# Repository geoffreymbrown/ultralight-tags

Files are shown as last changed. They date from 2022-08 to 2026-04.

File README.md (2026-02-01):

See [Documentation](https://geoffreymbrown.github.io/ultralight-tags/) to explore this project and for complete build instructions.

# building with OS X

cmake  -DQt6_DIR=/Users/geobrown/Qt/6.5.3/macos  ~/Research/ultralight-tags 

Make sure to add Qt-version/bin (or current version) to your path so that the various find_program tools work (esp macdeployqt)

(use your signing authority)

macdeployqt bin/btviz.app -codesign="Indiana University"
macdeployqt bin/qtmonitor.app -codesign="Indiana University (5J69S77A7G)"
macdeployqt bin/tag-test.app -codesign="Indiana University"
        
To verify

codesign --verify --deep --verbose xyz.app

Then build the dmg file

cpack -G DragNDrop

No longer building qt -- using distributed version
-------------

Building QT

https://doc.qt.io/qt-6/macos-building.html

_ ./configure -- -DCMAKE_OSX_ARCHITECTURES="x86_64h;arm64"

Install	macports

sudo port install libusb-1.0
#sudo port install qt6

# building with MSVC

you have my deepest sympathy

## For building host software    

* install vcpkg -- within vcpkg:
  * install protobuf --- vcpkg.exe install protobuf --triplet=x64-windows-static
  * install qt:x64-windows-static
  * install libusb:x64-windows-static
  * install ms-angle:x64-windows-static
* install nanopb binary  -- unpack in root_dir/nanopb ;   using the binary version is more reliable than using the source version
* install pkg-config choco install pkgconfiglite -y

**Note** cmake now understands vcpkg so the direct installation within vcpkg is no longer needed.   Instead there are json files in the ultralight-tags directory that cmake uses in install vcpkg files.

### Configure main build

cmake -DVCPKG_TARGET_TRIPLET="x64-mingw-static" -G "MinGW Makefiles" -DCMAKE_TOOLCHAIN_FILE="d:/vcpkg/scripts/buildsystems/vcpkg.cmake" c:/Users/geobrown/ultralight-tags

**Note** cmake has trouble on windows finding Qt.  The workaround is to use qt-cmake from the qt installation.

```
  cmake -DVCPKG_TARGET_TRIPLET="x64-windows-static" -DCMAKE_TOOLCHAIN_FILE="c:/users/geoff/vcpkg/scripts/buildsystems/vcpkg.cmake" c:/Users/geoff/ultralight-tags
```

```
qt-cmake -B Build -S c:\users\geobrown\ultralight-tags --preset default -G "Visual Studio 17 2022"
```

### Build release/debug

```
cmake --build . --config Debug  
cmake --build . --config Release
```

## Building Embedded Software

* install ChibiOS (submodule in repo)
* install gnu-arm toolchain
* install java
* install fmpp
* install make (choco)

### Building Tags

```
cmake --build . --target [BitTagv6|BitTagv5|BitTagNucleo]
cmake --build . --target BitTagv6-download

```

### Building Base boards

```
cmake --build . --target bittag-base-jlcpcb-v3
cmake --build . --target bittag-base-jlcpcb-v3-dfu
cmake --build . --target tag-breakout-base-jlcpcb32-v1
cmake --build . --target tag-breakout-base-jlcpcb32-v1-dfu
```

 The -dfu rule attempts to  program the board.

## Programming Embedded Hardware

* Install [stm32cube programmer](https://wiki.st.com/stm32mpu/wiki/STM32CubeProgrammer)

## Programming with STM32Cube Programmer

```
~/Software/STM32CubeProgrammer/bin/STM32_Programmer_CLI.exe -c port=SWD mode=UR -d ch.elf -v -g 0x08000000 
```

* `port=SWD` driver
* `mode=UR` -- attach under reset
* `-g 0x08000000`  -- execute program after completion
* `-v` verify
* `-vb 3`  verbose logging (for debugging)

### DFU for base boards

Make sure a device is in dfu mode

```
STM32_Programmer_CLI.exe -l usb
```

To program from command line

```
 ~/Software/STM32CubeProgrammer/bin/STM32_Programmer_CLI -c port=usb1 -d build/ch.elf 
 ```

## Installing protobuf on linux

```
git clone https://github.com/google/protobuf.git
cd protobuf
configure
make 
sudo make install
mkdir build
cd build
cmake ../cmake
make
sudo make install
```

# Tools

## Host and Embedded 

cmake
protobuf -- protoc, libprotobuf, python (pip install protobuf)
nanopb
python

## Host only

Qt5
libusb
vcpkg (windows)

## Embedded only

chibios
fmpp
stm32 programmer cli
arm gcc tools

## Mechanical

openscad 
kicad

## Powershell $Profile

$env:Path += ";C:\Program Files (x86)\GNU Arm Embedded Toolchain\9 2020-q2-update\bin\"
$env:Path += "; C:\Program Files (x86)\Microsoft Visual Studio\2019\Community\VC\Tools\MSVC\14.27.29110\bin\Hostx64\x64\"
$env:Path += "; C:\Program Files (x86)\Microsoft Visual Studio\2019\Community\VC\Tools\MSVC\14.27.29110\bin\Hostx64\x86\"
$env:Path += "; C:\Program Files\fmpp\bin"
$env:Path += "; C:\Program Files\Java\jre1.8.0_261\bin"
$env:Path += "; C:\Program Files\STMicroelectronics\STM32Cube\STM32CubeProgrammer\bin"
$env:Path += "; C:\Program Files (x86)\Microsoft Visual Studio\2019\Community\SDK\ScopeCppSDK\vc15\SDK\bin"

# Notes on universal binary

cmake ~/Research/ultralight-tags    -DCMAKE_OSX_ARCHITECTURES="x86_64;arm64" -DCMAKE_OSX_DEPLOYMENT_TARGET="12.3"

libusb

 ./configure CFLAGS="-arch x86_64 -arch arm64" CXXFLAGS="-arch x86_64 -arch arm64"

 protobuf

 ./configure CFLAGS="-arch x86_64 -arch arm64" CXXFLAGS="-arch x86_64 -arch arm64"

 # Notes on Building Static qt for windows

 - Download sources
 - use ""x64 Native Tools Command Prompt for VS 2022" for building !!  This is important because otherwise the powershell window will build a 32bit binary
 - 
 - ..\Qt\6.10.2\Src\configure.bat -prefix C:\QT-build\ -static -static-runtime -release -nomake examples -nomake tests --skip qtquick3dphysics --skip qtopcua
 - cmake --build .
 - cmake --install . --prefix c:\Qt6-static

 Fucking Windows 11 opens 32 bit developer powershell by default!  Have to find the 64 bit version in visual studio tools-commandline

 Open the Start Menu and search for the "x64 Native Tools Command Prompt" for your installed version of Visual Studio (e.g., "x64 Native Tools Command Prompt for VS 2022"). This ensures your environment variables are correctly set for a 64-bit build.

 Building for windows 2/1/26

- $env:Qt6_DIR = "C:\Qt6-static\lib\cmake\Qt6\"  
- cmake -DVCPKG_TARGET_TRIPLET="x64-windows-static" -DCMAKE_TOOLCHAIN_FILE="c:/users/geoff/vcpkg/scripts/buildsystems/vcpkg.cmake" -D Qt6_DIR="c:/Qt6-static/lib/cmake/Qt6" c:/Users/geoff/ultralight-tags

- cmake --Build . --config Release  
- cmake --install . --prefix install-directory-path

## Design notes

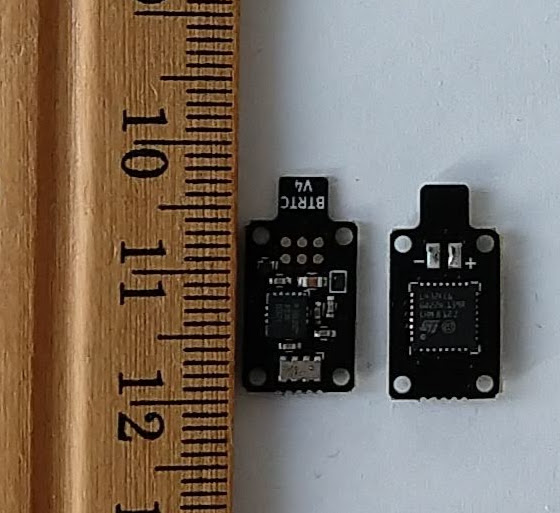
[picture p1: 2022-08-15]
docs/content/en/docs/architecture/images/bittagsbothsides.jpg

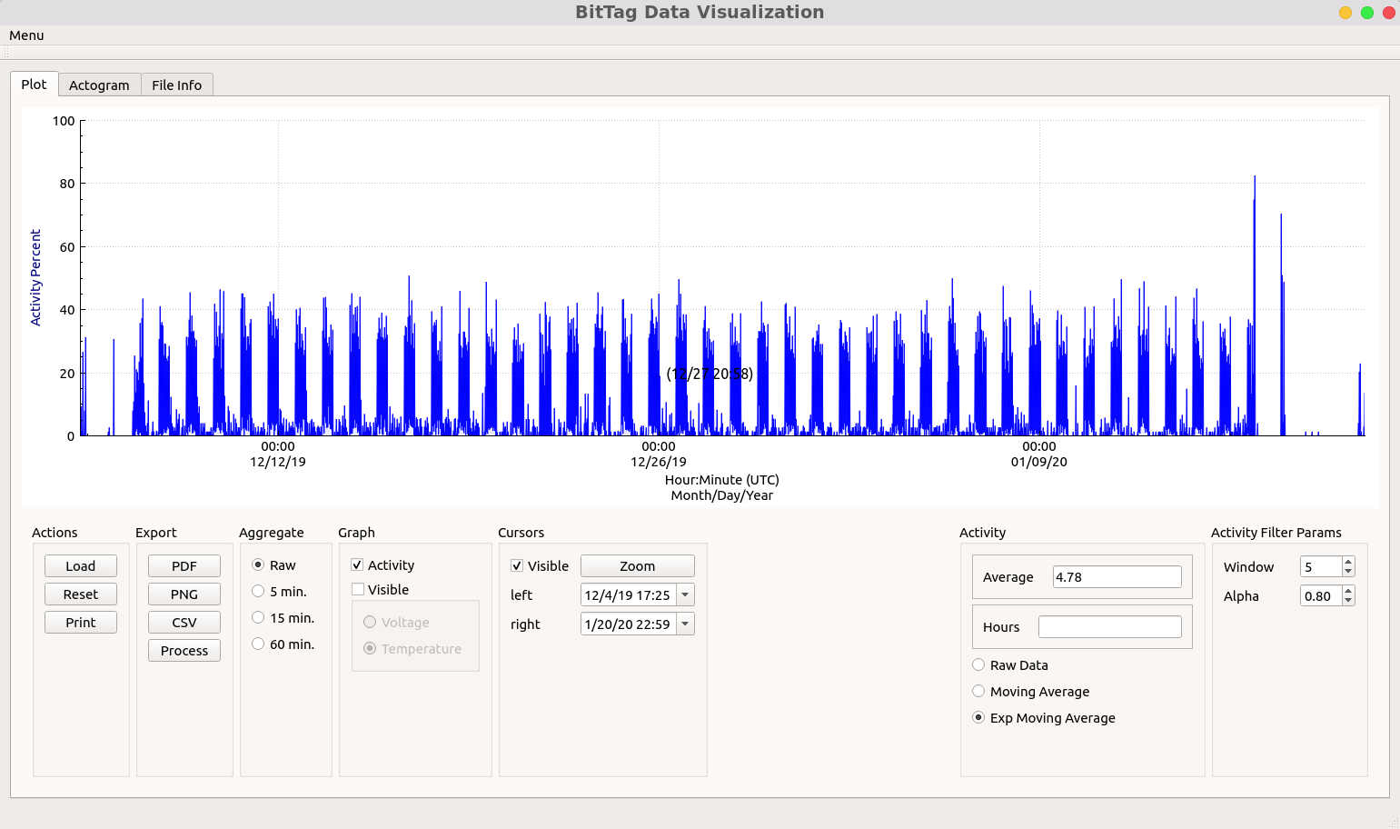
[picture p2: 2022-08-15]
docs/content/en/docs/architecture/images/datavisualization.png

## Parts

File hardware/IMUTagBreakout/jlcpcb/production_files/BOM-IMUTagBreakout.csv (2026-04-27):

Comment | Designator | Footprint | LCSC | Quantity
0.1uf | C1,C10,C2,C5,C6,C7,C8,C9 | C_0603_1608Metric | C14663 | 8
1uf | C3,C4 | C_0603_1608Metric | C15849 | 2
220 | R1,R2 | R_0603_1608Metric | C22962 | 2
AK09940A | U3 | AK09940a | C6794828 | 1
LED | D1,D2 | LED_0603_1608Metric | C2286 | 2
LPS22HH | U5 | ST_HLGA-10_2x2mm_P0.5mm_LayoutBorder3x2y | C2827824 | 1
LSM6DSV16XTR | U4 | LGA-14_3x2.5mm_P0.5mm_LayoutBorder3x4y | C5267406 | 1
MX25L12835G | U2 | SOIC-8_5.3x6.2mm_P1.27mm | C136615 | 1
TPS7A0218PDQNR | U1 | Texas_X2SON-4_1x1mm_P0.65mm | C2862166 | 1

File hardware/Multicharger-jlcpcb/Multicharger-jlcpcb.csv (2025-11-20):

Source: | /home/geobrown/Research/ultralight-tags/hardware/Multicharger-jlcpcb/Multicharger-jlcpcb.kicad_sch
Date: | Sun 09 Jul 2023 01:42:09 PM EDT
Tool: | Eeschema 6.0.11-2627ca5db0~126~ubuntu22.04.1
Generator: | /usr/share/kicad/plugins/bom_csv_grouped_by_value_with_fp.py
Component Count: | 20
Ref | Qnty | Value | Cmp name | Footprint | Description | Vendor
C101, | 1 | 0.1uF | C | Capacitor_SMD:C_0402_1005Metric | Unpolarized capacitor
C106, | 1 | 1uF | C | Capacitor_SMD:C_0402_1005Metric | Unpolarized capacitor
C107, | 1 | 2.2uF | C | Capacitor_SMD:C_0402_1005Metric | Unpolarized capacitor
D101, | 1 | No Go Red | LED | LED_SMD:LED_0603_1608Metric | Light emitting diode
D102, | 1 | BLUE | LED | LED_SMD:LED_0603_1608Metric | Light emitting diode
D103, | 1 | Go Green | LED | LED_SMD:LED_0603_1608Metric | Light emitting diode
D104, D105, | 2 | D_Schottky | D_Schottky | Diode_SMD:D_SOD-323 | Schottky diode
J104, | 1 | USB_B_Mini | USB_B_Mini | Connector_USB:USB_Mini-B_Lumberg_2486_01_Horizontal | USB Mini Type B connector
R1, | 1 | 680 | R | Resistor_SMD:R_0603_1608Metric | Resistor
R101, | 1 | 220 | R | Resistor_SMD:R_0603_1608Metric | Resistor
R102, R105, | 2 | 120 | R | Resistor_SMD:R_0603_1608Metric | Resistor
R103, | 1 | 91K | R | Resistor_SMD:R_0603_1608Metric | Resistor
R104, | 1 | 13K | R | Resistor_SMD:R_0603_1608Metric | Resistor
R106, | 1 | 1500 | R | Resistor_SMD:R_0603_1608Metric | Resistor
R107, | 1 | 2.2K | R | Resistor_SMD:R_0603_1608Metric | Resistor
SW101, | 1 | SW_DIP_x04 | SW_DIP_x04 | Button_Switch_SMD:SW_DIP_SPSTx04_Slide_6.7x11.72mm_W8.61mm_P2.54mm_LowProfile | 4x DIP Switch, Single Pole Single Throw (SPST) switch, small symbol
U101, | 1 | TPS3700 | TPS3700 | Package_TO_SOT_SMD:SOT-23-6
U106, | 1 | XC6206-3.3V | XC6206PxxxMR | Package_TO_SOT_SMD:SOT-23-3 | Positive 60-250mA Low Dropout Regulator, Fixed Output, SOT-23

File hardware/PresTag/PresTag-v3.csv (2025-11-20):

Source: | /home/geobrown/Research/ultralight-tags/hardware/PresTag/PresTag-v3.kicad_sch
Date: | Thu 16 Mar 2023 07:56:26 PM EDT
Tool: | Eeschema 6.0.2+dfsg-1
Generator: | /usr/share/kicad/plugins/bom_csv_grouped_by_value.py
Component Count: | 20
Individual Components:
Item | Qty | Reference(s) | Value | LibPart | Footprint | Datasheet | Config | DISTPN | DNP | MFN | MPN | Macrofab | Populate
 |  | C1 | 0.1uf | Device:C | Capacitor_SMD:C_0201_0603Metric | ~ |  | 490-10403-1-ND |  | Murata | GRM033C81E104KE14D | MF-CAP-0402-0.1uF
 |  | C2 | 0.1uf | Device:C | Capacitor_SMD:C_0201_0603Metric | ~ |  | 490-10403-1-ND |  | Murata | GRM033C81E104KE14D | MF-CAP-0402-0.1uF
 |  | C101 | 1uf | Device:C | Capacitor_SMD:C_0201_0603Metric | ~ |  | 490-7229-1-ND |  | Murata | GRM033R60J105MEA2D
 |  | C404 | 22uf | Device:C | Capacitor_SMD:C_0402_1005Metric | ~ |  | 478-9839-1-ND |  | AVX | 04026D226MAT2A
 |  | C501 | 0.1uf | Device:C | Capacitor_SMD:C_0201_0603Metric | ~ |  | 490-10403-1-ND |  | Murata | GRM033C81E104KE14D | MF-CAP-0402-0.1uF
 |  | C502 | 0.1uf | Device:C | Capacitor_SMD:C_0201_0603Metric | ~ |  | 490-10403-1-ND |  | Murata | GRM033C81E104KE14D | MF-CAP-0402-0.1uF
 |  | C503 | 0.1uf | Device:C | Capacitor_SMD:C_0201_0603Metric | ~ |  | 490-10403-1-ND |  | Murata | GRM033C81E104KE14D | MF-CAP-0402-0.1uF
 |  | D401 | D | Device:D_Schottky | Diode_SMD:D_0402_1005Metric | ~ |  | 641-1519-1-ND |  | COMCHIP | CDBQC0130L-HF
 |  | J201 | CONN_02X04 | Connector_Generic:Conn_02x03_Odd_Even | bittag:tagpoints6 | ~ | DNF |  | 1 |  |  |  | No
 |  | J301 | Conn_01x01 | Mechanical:MountingHole | library:taghole1.1mm | ~ | DNF |  | 1 |  |  |  | No
 |  | J302 | Conn_01x01 | Mechanical:MountingHole | library:taghole1.1mm | ~ | DNF |  | 1 |  |  |  | No
 |  | J303 | Conn_01x01 | Mechanical:MountingHole | library:taghole1.1mm | ~ | DNF |  | 1 |  |  |  | No
 |  | J304 | Conn_01x01 | Mechanical:MountingHole | library:taghole1.1mm | ~ | DNF |  | 1 |  |  |  | No
 |  | J401 | CONN_01X02 | Connector_Generic:Conn_01x02 | bittag:MS621 | ~ | DNF |  | 1 |  |  |  | No
 |  | Q501 | Q_NPN_BEC | Device:Q_NPN_BEC | Package_TO_SOT_SMD:SOT-883 | ~ |  | 1727-2632-1-ND |  | Nexperia | BC847AMB,315
 |  | R1 | 10k | Device:R | Resistor_SMD:R_0201_0603Metric | ~ |  | 311-10.0KMCT-ND |  | Yaego | RC0201FR-0710KL | MF-RES-0402-10K
 |  | U1 | at25ex321D-UUN | at25xe:at25ex321D-UUN | library:adesto_wlcsp12 |  |  | 1265-AT25XE321D-UUN-TCT-ND |  | adesto | AT25XE321D-UUN-T
 |  | U2 | LPS27HHWTR | lps27:LPS27HHWTR | lib_fp:LPS27HHWTR |  |  | 497-LPS27HHWCT-ND |  | STMicroelectronics | LPS27HHWTR
 |  | U302 | stm32l431kc | PresTag-v3-rescue:stm32l432-gpsparts | Package_DFN_QFN:QFN-32-1EP_5x5mm_P0.5mm_EP3.45x3.45mm |  |  | 511-STM32L431KCU6 |  | STMicroelectronics | STM32L431KCU6
 |  | U501 | RV-3028-C7 | PresTag-v3-rescue:RV-3028-C7-gpsparts | library:RV-8803-C7 |  |  | 2195-RV-3028-C732.768KHZ1PPM-TA-QCCT-ND |  | Micro Crystal | RV-3028-C7 32.768KHZ 1PPM-TA-QC
Collated Components:
Item | Qty | Reference(s) | Value | LibPart | Footprint | Datasheet | Config | DISTPN | DNP | MFN | MPN | Macrofab | Populate
1 | 5 | C1, C2, C501, C502, C503 | 0.1uf | Device:C | Capacitor_SMD:C_0201_0603Metric | ~ |  | 490-10403-1-ND |  | Murata | GRM033C81E104KE14D | MF-CAP-0402-0.1uF
2 | 1 | C101 | 1uf | Device:C | Capacitor_SMD:C_0201_0603Metric | ~ |  | 490-7229-1-ND |  | Murata | GRM033R60J105MEA2D
3 | 1 | C404 | 22uf | Device:C | Capacitor_SMD:C_0402_1005Metric | ~ |  | 478-9839-1-ND |  | AVX | 04026D226MAT2A
4 | 1 | D401 | D | Device:D_Schottky | Diode_SMD:D_0402_1005Metric | ~ |  | 641-1519-1-ND |  | COMCHIP | CDBQC0130L-HF
5 | 1 | J201 | CONN_02X04 | Connector_Generic:Conn_02x03_Odd_Even | bittag:tagpoints6 | ~ | DNF |  | 1 |  |  |  | No
6 | 4 | J301, J302, J303, J304 | Conn_01x01 | Mechanical:MountingHole | library:taghole1.1mm | ~ | DNF |  | 1 |  |  |  | No
7 | 1 | J401 | CONN_01X02 | Connector_Generic:Conn_01x02 | bittag:MS621 | ~ | DNF |  | 1 |  |  |  | No
8 | 1 | Q501 | Q_NPN_BEC | Device:Q_NPN_BEC | Package_TO_SOT_SMD:SOT-883 | ~ |  | 1727-2632-1-ND |  | Nexperia | BC847AMB,315
9 | 1 | R1 | 10k | Device:R | Resistor_SMD:R_0201_0603Metric | ~ |  | 311-10.0KMCT-ND |  | Yaego | RC0201FR-0710KL | MF-RES-0402-10K
10 | 1 | U1 | at25ex321D-UUN | at25xe:at25ex321D-UUN | library:adesto_wlcsp12 |  |  | 1265-AT25XE321D-UUN-TCT-ND |  | adesto | AT25XE321D-UUN-T
11 | 1 | U2 | LPS27HHWTR | lps27:LPS27HHWTR | lib_fp:LPS27HHWTR |  |  | 497-LPS27HHWCT-ND |  | STMicroelectronics | LPS27HHWTR
12 | 1 | U302 | stm32l431kc | PresTag-v3-rescue:stm32l432-gpsparts | Package_DFN_QFN:QFN-32-1EP_5x5mm_P0.5mm_EP3.45x3.45mm |  |  | 511-STM32L431KCU6 |  | STMicroelectronics | STM32L431KCU6
13 | 1 | U501 | RV-3028-C7 | PresTag-v3-rescue:RV-3028-C7-gpsparts | library:RV-8803-C7 |  |  | 2195-RV-3028-C732.768KHZ1PPM-TA-QCCT-ND |  | Micro Crystal | RV-3028-C7 32.768KHZ 1PPM-TA-QC

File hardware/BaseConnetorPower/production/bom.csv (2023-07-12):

Designator | Footprint | Quantity | Value | LCSC Part #
C101 | 0402 | 1 | 0.1uF | C1525
C106 | 0402 | 1 | 1uF | C52923
C107 | 0402 | 1 | 2.2uF | C12530
D101 | 0603 | 1 | No Go Red | C2286
D102 | 0603 | 1 | BLUE | C72041
D103 | 0603 | 1 | Go Green | C72043
D104 | D_SOD-323 | 1 | D_Schottky | C191023
J104 | USB_Mini-B_Lumberg_2486_01_Horizontal | 1 | USB_B_Mini | C2681563
R1 | 0603 | 1 | 680 | C23228
R101 | 0603 | 1 | 330 | C23138
R102, R105 | 0603 | 2 | 220 | C22962
R103 | 0603 | 1 | 91K | C23265
R104 | 0603 | 1 | 13K | C22797
R106 | 0603 | 1 | 1500 | C22843
R107 | 0603 | 1 | 2.2K | C4190
SW101 | SW_DIP_SPSTx04_Slide_6.7x11.72mm_W8.61mm_P2.54mm_LowProfile | 1 | SW_DIP_x04 | C3034155
U101 | SOT-23-6 | 1 | TPS3700 | C3658987
U106 | SOT-23-3 | 1 | AP7370 | C3745233

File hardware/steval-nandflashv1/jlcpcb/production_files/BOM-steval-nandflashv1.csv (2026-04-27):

Comment | Designator | Footprint | LCSC | Quantity

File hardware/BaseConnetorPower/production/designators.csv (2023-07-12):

C101:1
C106:1
C107:1
D101:1
D102:1
D103:1
D104:1
J101:1
J102:1
J103:1
J104:1
MK101:1
MK102:1
MK103:1
MK104:1
R1:1
R101:1
R102:1
R103:1
R104:1
R105:1
R106:1
R107:1
R2:1
SW101:1
U101:1
U106:1

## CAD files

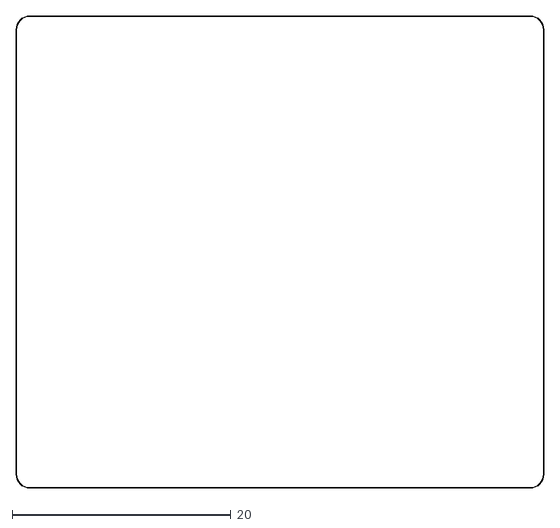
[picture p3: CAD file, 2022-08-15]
hardware/BaseConnetorPower/Drawings/MultiCharger-Edge_Cuts.dxf
48.3 x 43.2

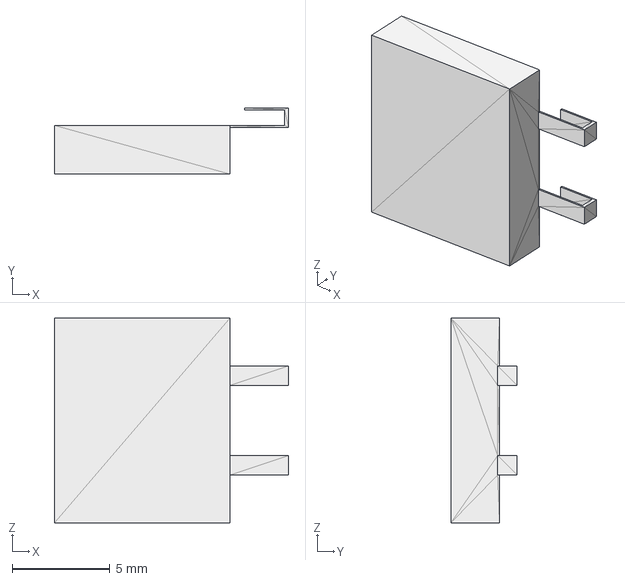
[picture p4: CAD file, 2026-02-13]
hardware/imutag-4layer/lipo.step
12.0 x 3.40 x 10.5 mm

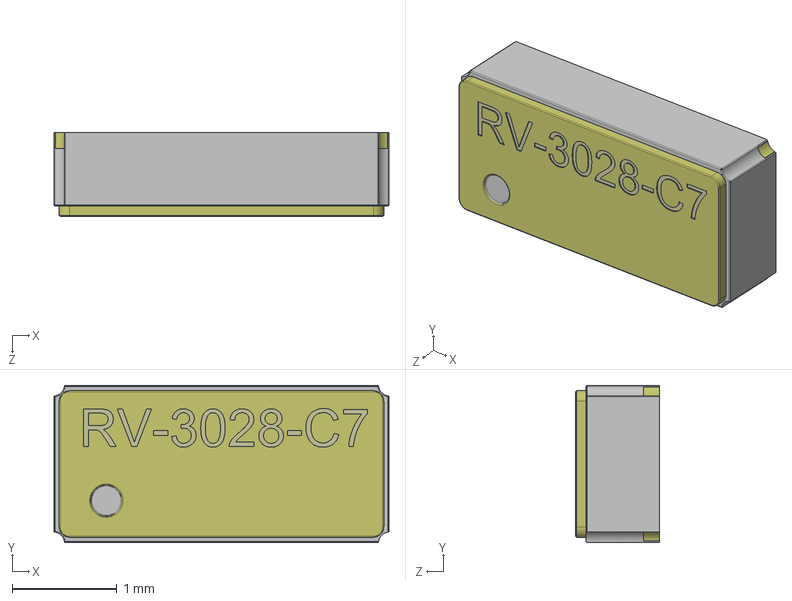
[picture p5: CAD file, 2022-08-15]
hardware/IMUTagBreakout/RV3028.step
3.20 x 1.50 x 0.8 mm

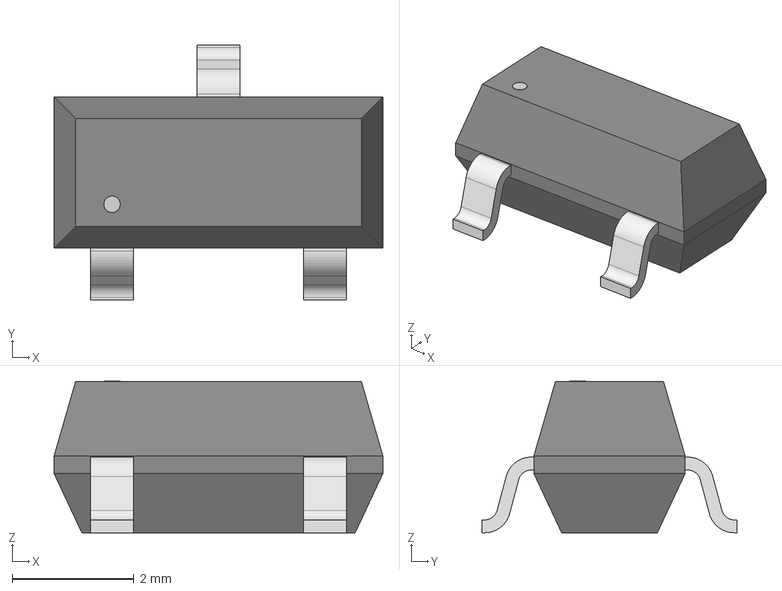
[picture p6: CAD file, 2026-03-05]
hardware/kicad_libraries/3d_models/CJS-1200B_NDC.step
5.41 x 4.19 x 2.49 mm

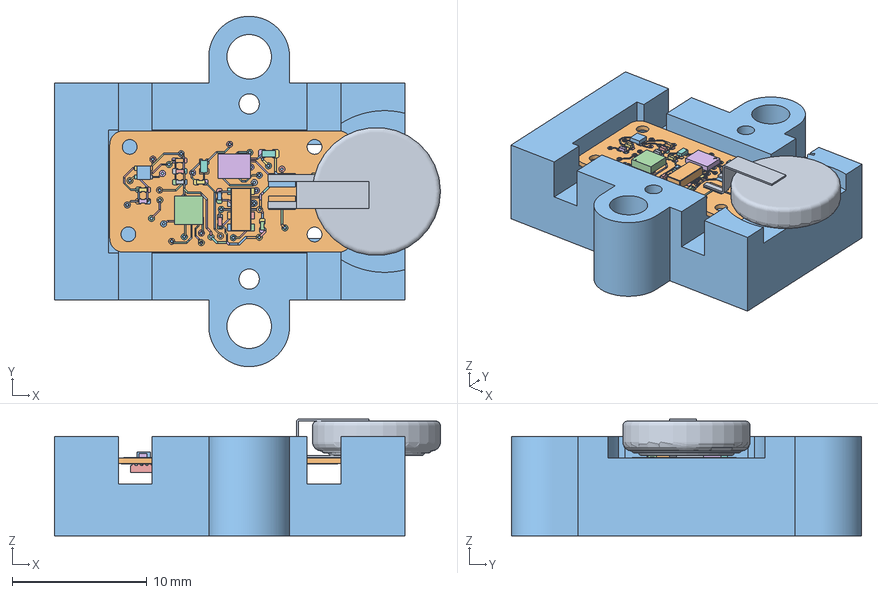
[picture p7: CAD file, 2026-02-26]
hardware/Mechanical/temp.FCStd
28.7 x 26.0 x 8.67 mm
MS920SE-FL27E
ASSEMBLY
R_0201_0603Metric
C_0201_0603Metric
C_0201_0603Metric002
C_0201_0603Metric004
Diodes_DFN1006_3
C_0201_0603Metric006
C_0201_0603Metric008
DQN4
C_0201_0603Metric010
C_0201_0603Metric012
C_0201_0603Metric014
C_0402_1005Metric
C_0402_1005Metric002
D_SOD_923
QFN-32-1EP_5x5mm_Pitch0.5mm
C_0201_0603Metric016
C_0201_0603Metric018
C_0603_1608Metric
CompassTag_track_1
CompassTag_track_2
CompassTag_track_3
CompassTag_track_5
CompassTag_track_6
CompassTag_track_7
CompassTag_track_8
CompassTag_track_9
CompassTag_track_10
CompassTag_track_11
CompassTag_track_12
CompassTag_track_13
CompassTag_track_14
CompassTag_track_15
CompassTag_track_16
CompassTag_track_18
CompassTag_track_19
CompassTag_track_20
CompassTag_track_21
CompassTag_track_22
CompassTag_track_23
CompassTag_track_24
CompassTag_track_25
CompassTag_track_26
CompassTag_track_27
CompassTag_track_28
CompassTag_track_29
CompassTag_track_30
CompassTag_track_31
CompassTag_track_32
CompassTag_track_33
CompassTag_track_34
CompassTag_track_35
CompassTag_track_36
CompassTag_track_37
CompassTag_track_38
CompassTag_track_39
CompassTag_track_40
CompassTag_track_41
CompassTag_track_42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

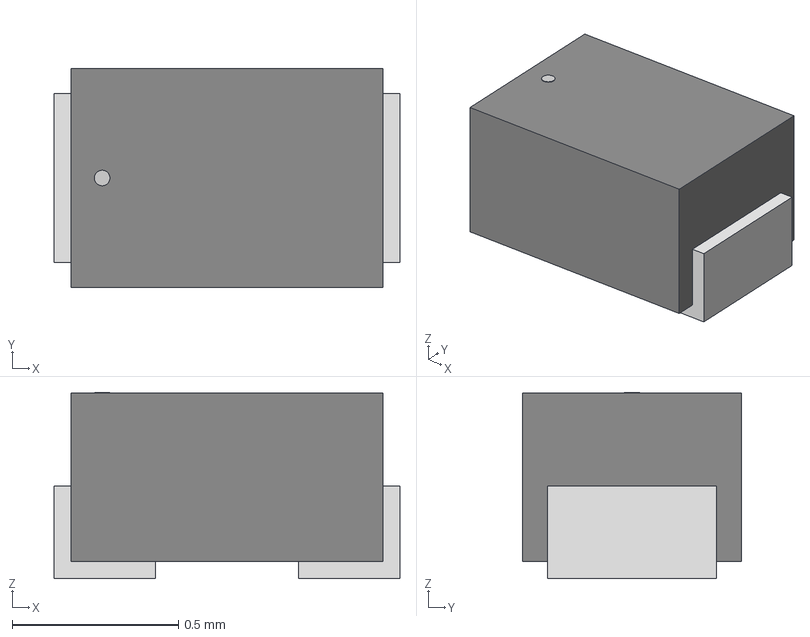
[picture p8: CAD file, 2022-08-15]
hardware/PresTag-v6/CDBQR.step
1.04 x 0.66 x 0.561 mm

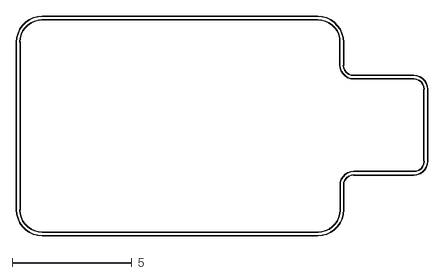
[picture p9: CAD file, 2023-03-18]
hardware/PresTag-v6/gerbers/PresTag-v3-Edge_Cuts.dxf
17.2 x 9.15

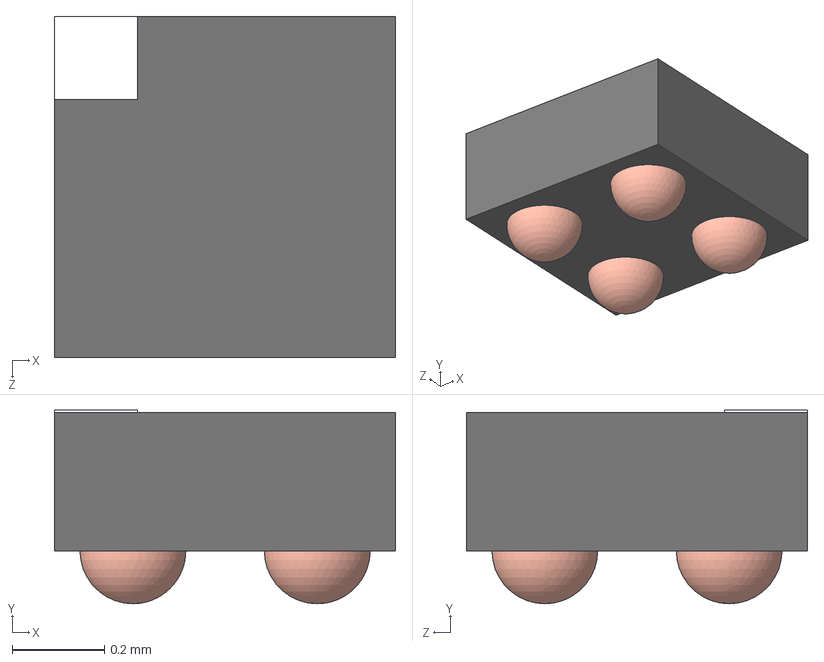
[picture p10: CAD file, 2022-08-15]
hardware/PresTagBMP581/DSBGA-4.step
0.74 x 0.42 x 0.74 mm

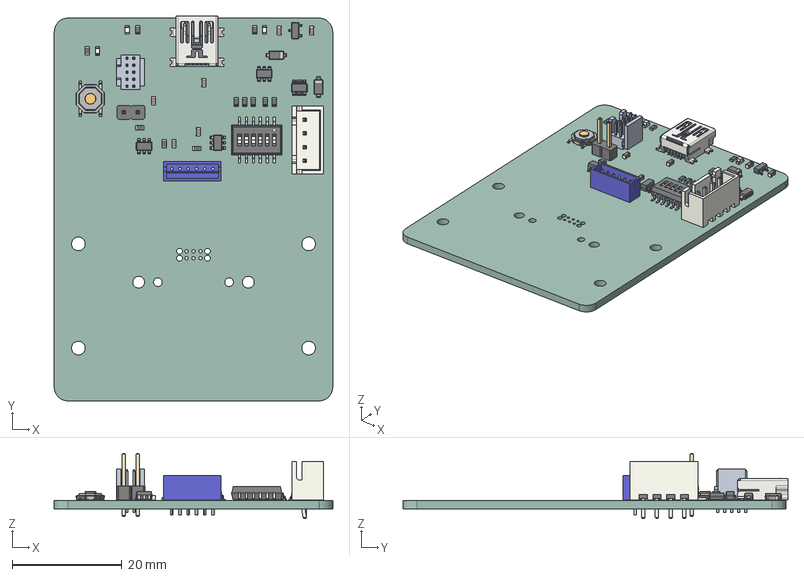
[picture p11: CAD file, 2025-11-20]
hardware/tagbase-jlcpcb-v7/tagbase-jlcpcb-v3.step
50.8 x 70.2 x 11.9 mm
LED_0603_1608Metric x 6
FTSH-105-01-F-D-K
SOT_23_6 x 6
SW_SPST_TL3342 x 2
SOT-23-3
SOT_23
USB_Mini-B_Lumberg_2486_01_Horizontal x 2
C_0603_1608Metric x 12
R_0603_1608Metric x 19
D_SOD_123 x 4
JST_B4B_XH_A x 2
SW_DIP_SPSTx06_Slide_KingTek_DSHP06TS_W762mm_P127mm
SOT_23_8
PinHeader_1x02_P254mm_Vertical x 2
B6B-ZR
_autosave-tagbase-jlcpcb-v3_PCB

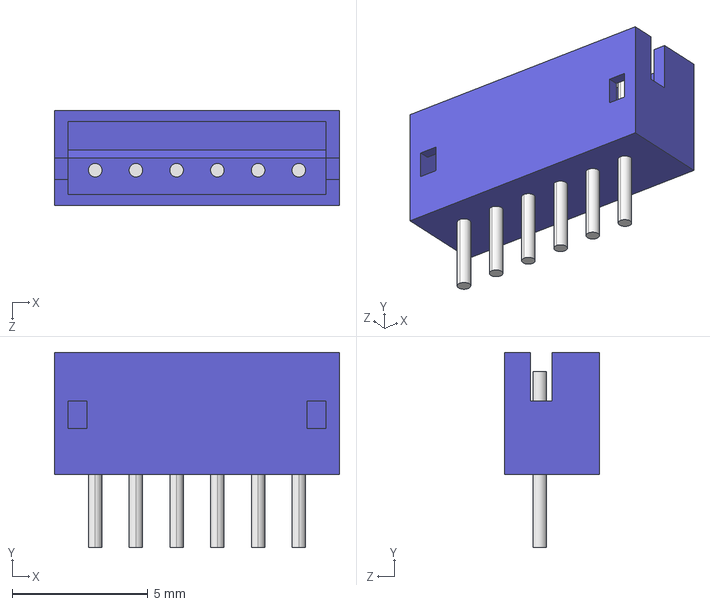
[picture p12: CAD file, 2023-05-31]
hardware/tagbase-lipo-v1/B6B-ZR.STEP
10.5 x 7.20 x 3.50 mm

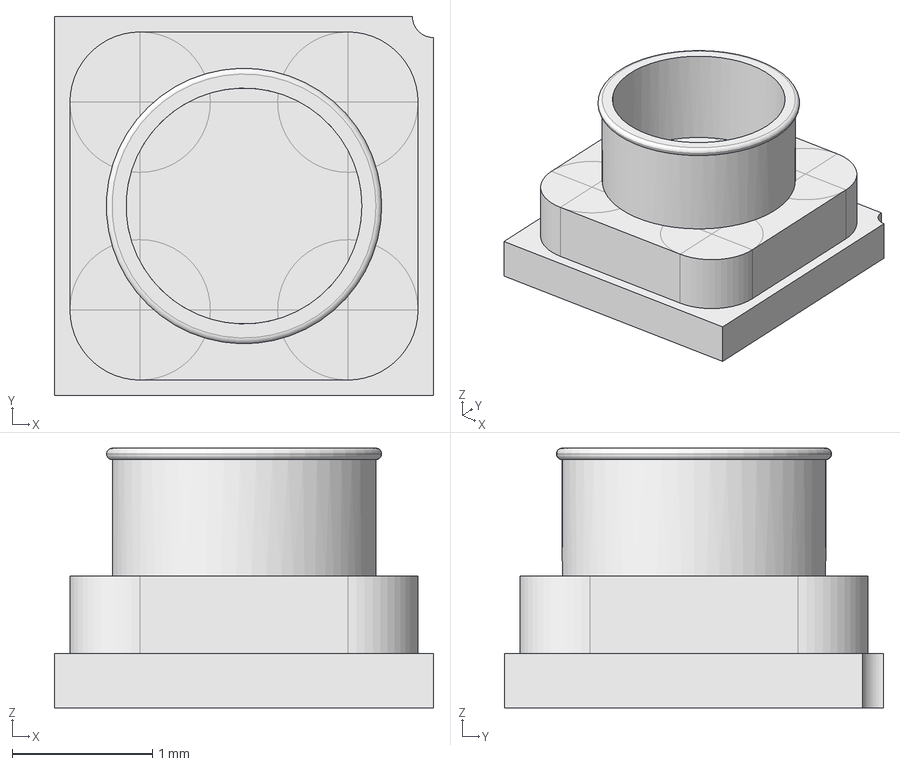
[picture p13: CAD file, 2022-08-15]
hardware/TagMagAccelPresBreakoutv2/lps27.step
2.70 x 2.70 x 1.85 mm

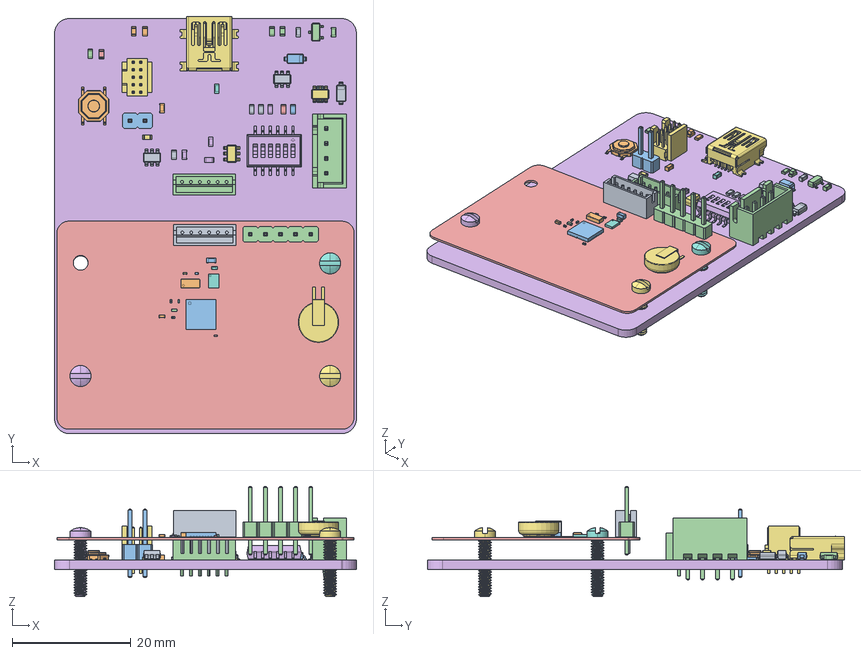
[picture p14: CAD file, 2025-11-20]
hardware/Templates/freecad/Unnamed.FCStd
50.8 x 70.2 x 18.5 mm
LED_0603_1608Metric
LED_0603_1608Metric002
LED_0603_1608Metric004
LED_0603_1608Metric006
LED_0603_1608Metric008
LED_0603_1608Metric010
FTSH-105-01-F-D-K
SOT_23_6
SOT_23_007
SW_SPST_TL3342
SW_SPST_TL3344
SOT-23-3
SOT_23
USB_Mini-B_Lumberg_2486_01_Horizontal
USB_Mini-B_Lumberg_2486_01_Horizontal002
C_0603_1608Metric
C_0603_1608Metric002
C_0603_1608Metric004
C_0603_1608Metric006
C_0603_1608Metric008
C_0603_1608Metric010
C_0603_1608Metric012
C_0603_1608Metric014
R_0603_1608Metric
R_0603_1608Metric002
R_0603_1608Metric004
R_0603_1608Metric006
R_0603_1608Metric008
R_0603_1608Metric010
R_0603_1608Metric012
R_0603_1608Metric014
R_0603_1608Metric016
R_0603_1608Metric018
R_0603_1608Metric020
R_0603_1608Metric022
R_0603_1608Metric024
R_0603_1608Metric026
R_0603_1608Metric028
SOT_23_008
R_0603_1608Metric030
R_0603_1608Metric032
D_SOD_123
D_SOD_124
JST_B4B_XH_A
JST_B4B_XH_A001
SW_DIP_SPSTx06_Slide_KingTek_DSHP06TS_W762mm_P127mm
SOT_23_009
SOT_23_8
SOT_23_010
SOT_23_011
PinHeader_1x02_P254mm_Vertical
PinHeader_1x02_P254mm_Vertical001
C_0603_1608Metric016
C_0603_1608Metric018
C_0603_1608Metric020
C_0603_1608Metric022
D_SOD_125
D_SOD_126
R_0603_1608Metric034
B6B-ZR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

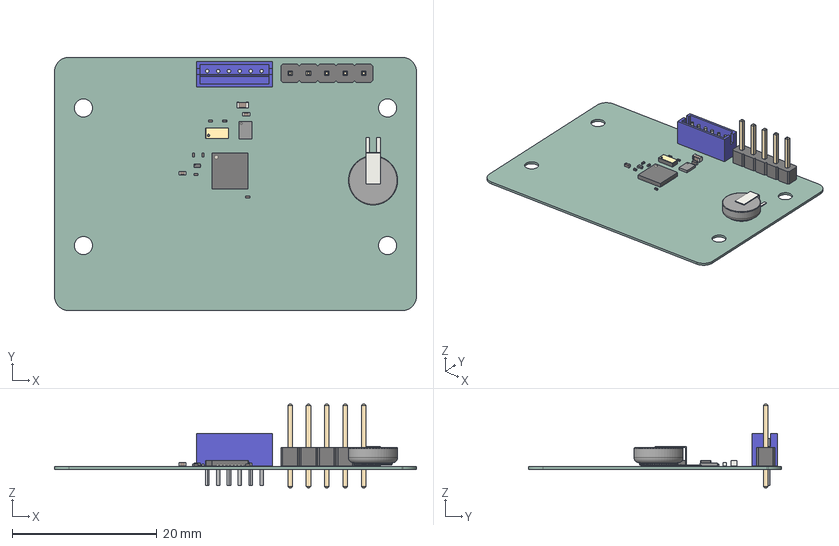
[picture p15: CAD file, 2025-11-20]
hardware/Templates/TagProto/TagProto.step
50.0 x 35.0 x 11.5 mm
Seiko_MS621F
C_0402_1005Metric x 3
ASSEMBLY
R_0201_0603Metric x 2
C_0201_0603Metric x 9
QFN-32-1EP_5x5mm_Pitch0.5mm
Diodes_DFN1006_3
B6B-ZR
C_0603_1608Metric
PinHeader_1x05_P254mm_Vertical
TagProto_PCB

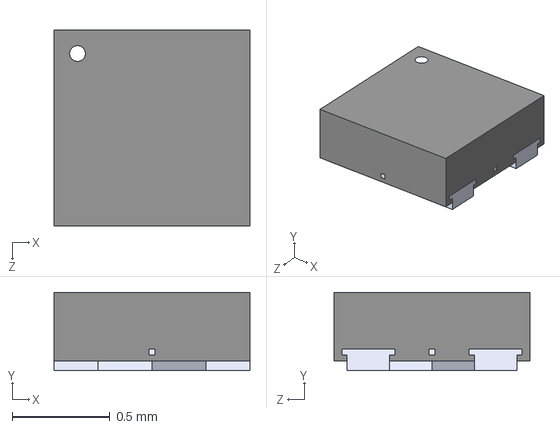
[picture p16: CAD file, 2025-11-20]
hardware/Templates/TagProtoLiPo/TPS7A0225PDQNR.step
1.00 x 0.4 x 1.00 mm

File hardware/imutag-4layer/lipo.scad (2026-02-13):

difference() {
    cube([4,1,5.6],true);
    cube([6,4,3.6],true);
    translate([-.3,0,0])cube([4.2,0.8,8],true);
    translate([-1.5,1.2,0])cube([2.5,3.1,8],true);
}
translate([-5.5,-1.65,0])cube([9,2.5,10.5],true);

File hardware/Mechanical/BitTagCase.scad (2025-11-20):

include  <roundedcube.scad>
$fn = 120; // steps in generating circles

// select parts

makelid = true;
makebase = true;

version_string = "BTCase"; // imprinted in base and lid

                // fiberglass thickness
pcb_thick     = 2.0;                    // pcb clearance  (for sweeping space)
pcb_clearance = 0.002*25.4;             // edge clearance (routing error)
pcb_len       = 14 + pcb_clearance*2;
pcb_width     = 9 + pcb_clearance*2;
   
lid_height = 3.5;

//
// dimensions of base
//

base_width       = pcb_width + 5.0;
base_len         = pcb_len + 14;
base_height      = 4;//1.5;  // base holds 1.5mm board
post_rad         = 2.0;                    // radius of post support
post_hole_insert = 0.75;                   // clearance for 2-56 insert
post_dist        = 17.0;                   // distance between posts


// helper function
// create a cube centered [x/2,y/2,0]

module centerCube(x,y,z) {
   translate([0,0,z/2]) cube([x,y,z],center=true);
}


// generate the PCB 




module makePCB(height) {
   centerCube(pcb_len,pcb_width,height);
    // battery
   translate([pcb_len/2.0+3,0,0])cylinder(r=5,h=height+2);
}


// make a crossbar with endholes -- we need two of these
// one for the base, one for the lid

module makeCrossBar(height,endheight,hole) {
   difference(){
             union(){
                   // cross piece
                centerCube(2*post_rad,post_dist,height);
                   // end cylinders
                translate([0,post_dist/2,0])
		            cylinder(r=post_rad, h=endheight);
                translate([0,-post_dist/2,0])
		            cylinder(r=post_rad, h=endheight);
               };
              union(){  // punch holes
               translate([0,post_dist/2,0])
                    cylinder(r=hole,h=endheight);
               translate([0,-post_dist/2,0])
                    cylinder(r=hole,h=endheight);
               };
      };
}

// make the base

module makeBase() {
     difference(){
           // positive -- box with cross bars
           union(){
            translate([0,0,-base_height/2])
                union(){
                    
                    // base cube
                    roundedcube([base_len,base_width,base_height],true,0.8,"z");
                    
                    // snap bar
                    
                    translate([0,0,0.85])centerCube(6,base_width+1.1,1);

                    // cross bars
                    
                    translate([-9,0,-2])makeCrossBar(base_height/2,base_height/2,post_hole_insert);
                    translate([ 10,0,-2])makeCrossBar(base_height/2,base_height/2,post_hole_insert);
                
                };
                
                // alignment pins
                 translate([base_len/2-2,base_width/2-2,0])cylinder(h=0.8,r=0.7);
                 translate([2-base_len/2,2-base_width/2,0])cylinder(h=0.8,r=0.7);
            }
        {
            // text
        
               translate([1,0,-base_height+.3])
                 rotate(a=[0,180,-90])linear_extrude(0.5)	
                 text(text=version_string,size=2,halign="center");
        };
    }
}


module snap(length){
     rotate([0,90,0]) linear_extrude(length)polygon(points=[[0,0],[4,0],[4,0.5],[3,1.25],[2.8,1.25],[2.8,0.8],[0,0.8]]);
    //linear_extrude(length)polygon(points=[[0,0],[4,0],[4,0.5],[2.5,2],[2.5,1],[0,1]]);
    
    
}

module makeLid(){
	translate([0,0,lid_height/2])
	        difference(){union(){
                roundedcube([base_len,base_width,lid_height],true,0.8,"z");
                translate([0,0,-lid_height/2 + 1])centerCube(5,base_width+2.9,lid_height-1);
                //translate([0,0,-lid_height/2-1])centerCube(base_len+2,8,lid_height+1);
               
                // snaps
                translate([-2.5,-8.5,-0.3])snap(5);
                rotate([0,0,180])translate([-2.5,-8.5,-0.3])snap(5);
            };
             // text
                 translate([-1,0,lid_height/2-0.5])
                 rotate(a=[0,0,-90])linear_extrude(0.6)	
                 text(text=version_string,size=2,halign="center");
            // alignment pin holes
                 translate([base_len/2-2,base_width/2-2,-1.8])cylinder(h=1,r=0.8);
                 translate([2-base_len/2,2-base_width/2,-1.8])cylinder(h=1,r=0.8);
            
            };
                 
}

if (makebase) 
{
      translate(makelid?[0,0,0]:[0,0,base_height])difference() {
        makeBase();
        #translate([-3,0,-base_height+1.25])makePCB(3);
   };

}

   
  //makePCB(3.5);

if (makelid) 
    
     color("green")rotate(makebase?[0,0,0]:[180,0,0])translate(makebase?[0,0,10]:[0,0,-lid_height])difference() {
     makeLid();
     translate([-3,0,-base_height+1.25])makePCB(3);
   }
   

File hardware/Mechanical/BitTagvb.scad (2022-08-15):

$fn = 120; // steps in generating circles

makelid = true;
makebase = true;

version_string = "BitTagVB"; // imprinted in base and lid

// helper function
// create a cube centered [x/2,y/2,0]

module centerCube(x,y,z) {
   translate([0,0,z/2]) cube([x,y,z],center=true);
}

//
// Parameters for test pins
// 
pogo_pin_height = 6.27-0.7;  // Pin height at pcb
pogo_box_len = 3.2;          // length of pogo pin group
pogo_box_width = 7;          // width of pogo pin group

//screw_rad = 1.0;


//
// PCB cutout and Base dimensions
// These neeed to be gathered from
// kicad pcb file
//
pcb_min_thick = 0.6;                   // fiberglass thickness
pcb_thick     = 4.0;                    // pcb clearance  (for sweeping space)
pcb_clearance = 0.006*25.4;             // edge clearance (routing error)
pcb_len       = 13.5 + pcb_clearance*2;
pcb_width     = 9 + pcb_clearance*2;
    // battery support lip, length is arbitrary since this is just
    // to punch a hole
lip_len   = 8;                    
lip_width = 4 + pcb_clearance*2;
lip_rad   = 0.5 + pcb_clearance;

cutclear = 1.5; // horizontal space around cutout under pcb (/2 on each edge) 
pogo_center = [4.385, 0.0];   // offset from board center of pogo pins

//
// dimensions of base
//

base_width       = pcb_width + 7.0;
base_len         = pcb_len + 8.0;
base_height      = pogo_pin_height + 2;//1.5;  // base holds 1.5mm board
cut_depth        = 1.5;                    // clearance under board
post_rad         = 3.0;                    // radius of post support
post_hole_insert = 1.65;                   // clearance for 2-56 insert
post_hole_screw  = 1.2;                    // clearance for 2-56 screw
post_off         = -5.0;                   // offset from pogo pin
post_dist        = 20.0;                   // distance between posts
align_pin_off    = [-5.0,6.5];             // alignment pin offset
align_pin_rad    = 0.75;                   // radius of alignment pin

// generate the PCB outline

module makePCB() {
  difference(){
      // positive
     union(){
           // main body
	 centerCube(pcb_len,pcb_width,pcb_thick);
           // lip
         translate([(pcb_len+lip_len)/2.0,0,0])
	     centerCube(lip_len,lip_width,pcb_thick);
       
           // boxes for radii
         translate([(pcb_len+lip_rad)/2.0,(lip_width+lip_rad)/2.0,0])
	     centerCube(lip_rad,lip_rad,pcb_thick);
         translate([(pcb_len+lip_rad)/2.0,-(lip_width+lip_rad)/2.0,0])
 	     centerCube(lip_rad,lip_rad,pcb_thick);
         
       };
     // negative -- cut radii
     union(){
         translate([pcb_len/2.0+lip_rad,lip_width/2.0+lip_rad,0])
		cylinder(r=lip_rad,h=pcb_thick);
         translate([pcb_len/2.0+lip_rad,-lip_width/2.0-lip_rad,0])
                cylinder(r=lip_rad,h=pcb_thick);
      }; 
   };
}

// make a crossbar with endholes -- we need two of these
// one for the base, one for the lid

module makeCrossBar(height,endheight,hole) {
   translate([pogo_center[0]+post_off, pogo_center[1],0])
   difference(){
             union(){
                   // cross piece
                centerCube(2*post_rad,post_dist,height);
                   // end cylinders
                translate([0,post_dist/2,0])
		            cylinder(r=post_rad, h=endheight);
                translate([0,-post_dist/2,0])
		            cylinder(r=post_rad, h=endheight);
               };
              union(){  // punch holes
               translate([0,post_dist/2,0])
                    cylinder(r=hole,h=endheight);
               translate([0,-post_dist/2,0])
                    cylinder(r=hole,h=endheight);
               };
      };
}

// make the base

module makeBase() {
      difference(){
           // positive -- box with cross bars
        translate([0,0,-pogo_pin_height])
	        union(){
                centerCube(base_len,base_width,base_height);
 	            makeCrossBar(base_height,base_height,post_hole_insert);
            };
	    // negative -- pcb cutout, pogopin cutout,
	    //             slots for harness thread,
	    //             alignment pins
        union(){
   	       translate([0,0,-cut_depth])
               union(){
	                 // pcb clearance
		
	                centerCube(pcb_len-cutclear, pcb_width-cutclear,
		                       pcb_thick+cut_depth);

                    // harness slots
		
  	                translate([-pcb_len/2.0+cutclear/2+1.25,0,0])
		                centerCube(2.5,base_width,pcb_thick+cut_depth);
                    translate([pcb_len/2.0-cutclear/2-1.25,0,0])
	                    centerCube(2.5,base_width,pcb_thick+cut_depth);
		   
  	                // cleanup
		
 	                translate([pcb_len/2.0-cutclear/2-1.25,base_width/2,0])
		                cylinder(r=1.25,h=pcb_thick+cut_depth);
   	                translate([pcb_len/2.0-cutclear/2-1.25,-base_width/2,0])
		                cylinder(r=1.25,h=pcb_thick+cut_depth);
  	             };

             // pogo pin cutout
	     
	        translate([pogo_center[0],pogo_center[1],-pogo_pin_height-0.1])
	            centerCube(pogo_box_len,pogo_box_width,pogo_pin_height+4.0);

             // alignment pins

            translate([pogo_center[0]+align_pin_off[0],
			           pogo_center[1]+align_pin_off[1],
			           -pogo_pin_height-0.1])
	                        cylinder(r=align_pin_rad,h=pcb_thick+pogo_pin_height);
  	        translate([pogo_center[0]+align_pin_off[0],
	                   pogo_center[1]-align_pin_off[1],
		               -pogo_pin_height-0.1])
  	                        cylinder(r=align_pin_rad,h=pcb_thick+pogo_pin_height);
             
             // text

            translate([-4,0,-pogo_pin_height+0.4])
                 rotate(a=[0,180,-90])linear_extrude(0.5)	
                 text(text=version_string,size=2,halign="center");

             // thin battery end
  // battery
         translate([pcb_len/2.0+6.5,0,pcb_min_thick])cylinder(r=6.5,h=pcb_thick);
	        translate([pcb_len/2 - 2,-7/2,0.6])
	         cube([5,7,pcb_thick]);
	               
        };
     };
}

module makeLid(){
	translate([0,0,10])difference(){
        union(){
         end_height = 4;
         end_length = 2;
         end_width = pcb_width - 1;
	     makeCrossBar(3,4,post_hole_screw);
	     // end pieces -- inset from pcb edge by 1.1
	     translate([-pcb_len/2+1.1,0,-end_height/2])
	         centerCube(end_length,end_width,end_height);
             // centered over the pogo pins
	     translate([pogo_center[0],pogo_center[1],-end_height/2])
	         centerCube(end_length,end_width,end_height);
             // body
	     translate([-pcb_len/2+0.1,-pcb_width/2,0])
	         cube([pcb_len/2-0.7 + pogo_box_len/2 + pogo_center[0],
		           pcb_width,3]);
        };
	     // text
  	     #translate([-1,0,2.5])
	     rotate(a=[0,0,-90])linear_extrude(0.6)
             text(text=version_string,size=2,halign="center",valign="center");
    }; // difference end
}

if (makebase) 
   difference() {
     makeBase();
     makePCB();
   };

if (makelid) makeLid();

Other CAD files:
hardware/imutag-4layer/LGA-12L_LIS2DU12_STM.step
hardware/Mechanical/CompassTagv1.scad
hardware/Mechanical/BitTagCase-base.stl
hardware/Mechanical/BitTagCase-basev2.stl
hardware/Mechanical/BitTagCase-basev3.stl
hardware/Mechanical/BitTagCase-basev4.stl
hardware/Mechanical/BitTagCase-lid.stl
hardware/Mechanical/BitTagCase-lidv2.stl
hardware/Mechanical/BitTagCase-lidv3.stl
hardware/Mechanical/BitTagCase-lidv4.stl
hardware/Mechanical/BitTagCase.stl
hardware/Mechanical/BitTagv7-Edge_Cuts.dxf
hardware/Mechanical/BitTagv7.step
hardware/Mechanical/BitTagvc-base.stl
hardware/Mechanical/BitTagvc-lid.stl
hardware/Mechanical/BitTagvc.stl
hardware/Mechanical/CompassTag.FCStd
hardware/Mechanical/CompassTagV1.FCStd
hardware/Mechanical/CompassTagv1.stl
hardware/Mechanical/CompassTagv1base.stl
hardware/Mechanical/CompassTagv1lid.stl
hardware/Mechanical/IMUTag.FCStd
hardware/Mechanical/PresOptTag-v1.dxf
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

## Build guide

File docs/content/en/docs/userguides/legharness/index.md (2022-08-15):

---
title: "Loop Harnesses"
type: docs
weight: 25
description: "Loop Leg Harness Construction"
bookToc: false
---

# Guide to Building Leg Loop Harness For Activity Loggers

*This material adapted from guide written by Dillon Gaugon*

{{< columns >}}

This guide demonstrates a  method to build a leg loop harness for use on birds. 

The following empirical formula, presented in [^1], provides an effective guide for ornithologists seeking to build
harnesses for data loggers and trackers.

$\texttt{harness span} = 14.16 + 8.34*\texttt{body mass}^{0.437}$

The formula, based upon published data from a variety of species should provide a reasonable starting point for size.

[^1]: Naef-Daenzer, Beat. *An allometric function to fit leg-loop harnesses to terrestrial birds*.  **Journal of Avian Biology**, 38:404-407, 2007.
<--->

<figure align="center">
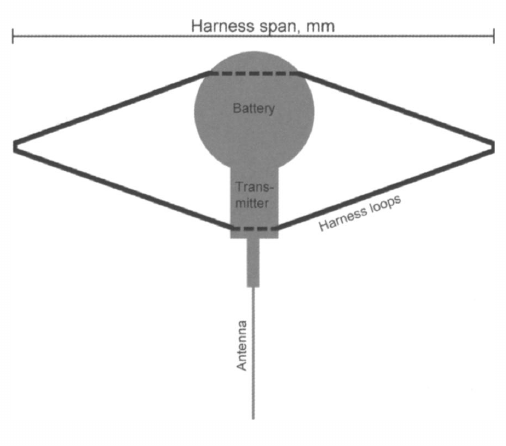
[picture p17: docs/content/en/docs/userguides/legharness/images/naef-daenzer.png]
Loop Harness

<figcaption align="center">Loop Harness: Naef-Daenzer 2007</figcaption>
</figure>

{{< /columns >}}

*For application of loggers with animals, an individual with the proper permits and training will need to be found or trained by someone with previous experience.*

## Step 1: Materials

{{< columns >}}

* First, you’ll need to gather your materials
* Six Thumbtacks
* Elastic bead cord 1mm (can be obtained at any arts and crafts store)
* Small scissors or a razor blade (needs to be sharp to cut string)
* Nail Polish (to glue knots together) or super glue
* White paint marker or sharpie (to mark the string)
* Ruler
* A corkboard
* A NanoTag Activity Logger

<--->

<figure align=center>
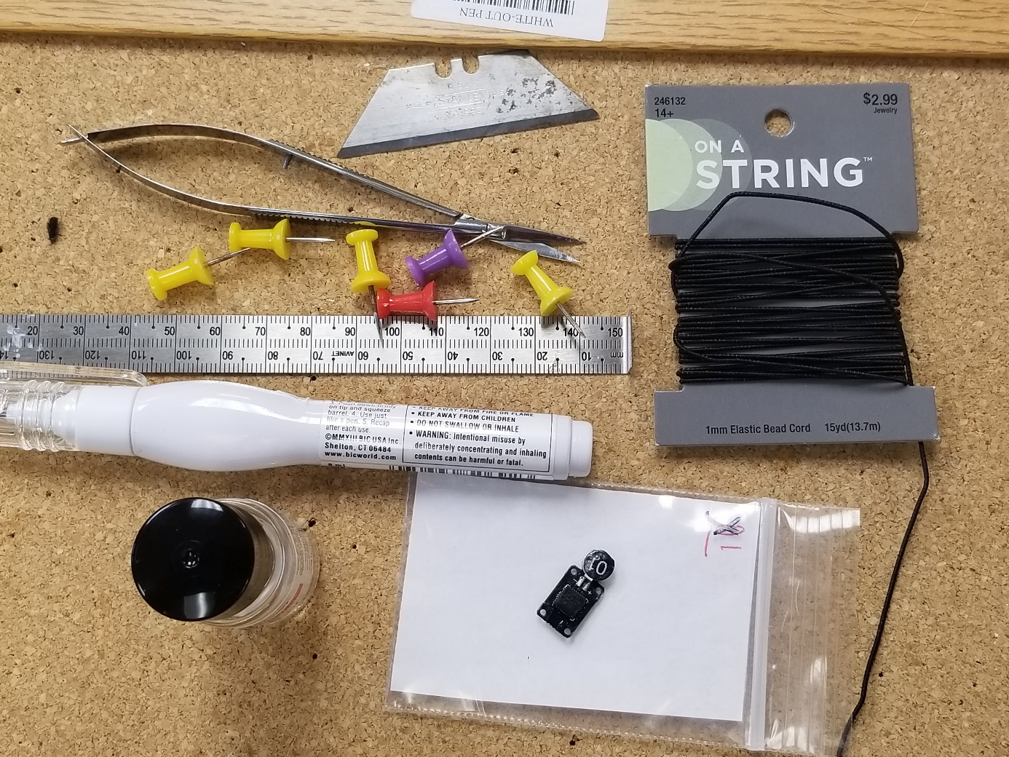
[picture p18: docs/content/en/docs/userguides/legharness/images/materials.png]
Harness Materials

<figcaption align=center>Fig. 1 Loop Harness Materials</figcaption>
</figure>

{{< /columns >}}

## Step 2:  Start Building !

{{< columns >}}

* Begin with a size in mind -- you will not be able to measure until later in the process; however, on Juncos we commonly use 42-44mm.
* Put the string through a hole on the opposite side of the battery.
* Put string through and leave about double the length of your desired size. So, for 40mm loggers, leave about 80mm.
* Make sure that the string does not go over the side with the gold dots! These will face down onto the bird’s back.

<--->

<figure align=center>
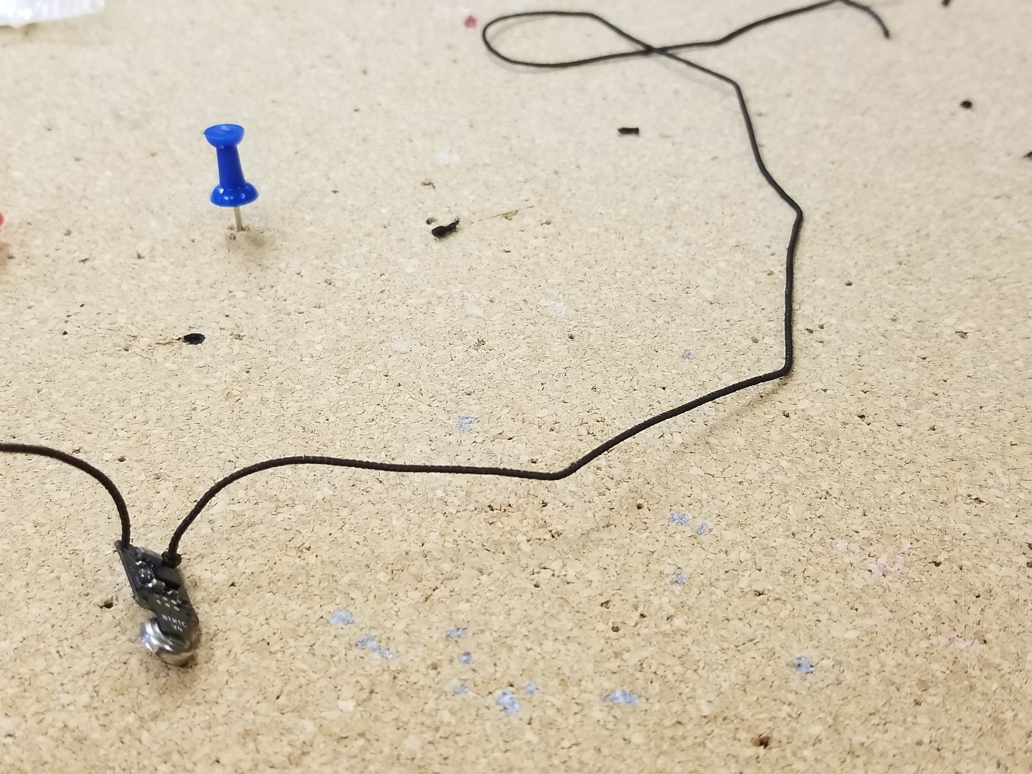
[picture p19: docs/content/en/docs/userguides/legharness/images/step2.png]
Start Building

<figcaption align=center>Fig. 2  Start Building</figcaption>
</figure>

{{< /columns >}}

## Step 3: Safety Knot !

{{< columns >}}

* Tie a knot at the base of the second hole that you will put the string through. Make sure you still leave plenty of string!
* Make sure it is set up so that the knot will stay at the base.
* To make charging easiest, check that the knot is not on the side with the gold dots!

<--->

<figure align=center>
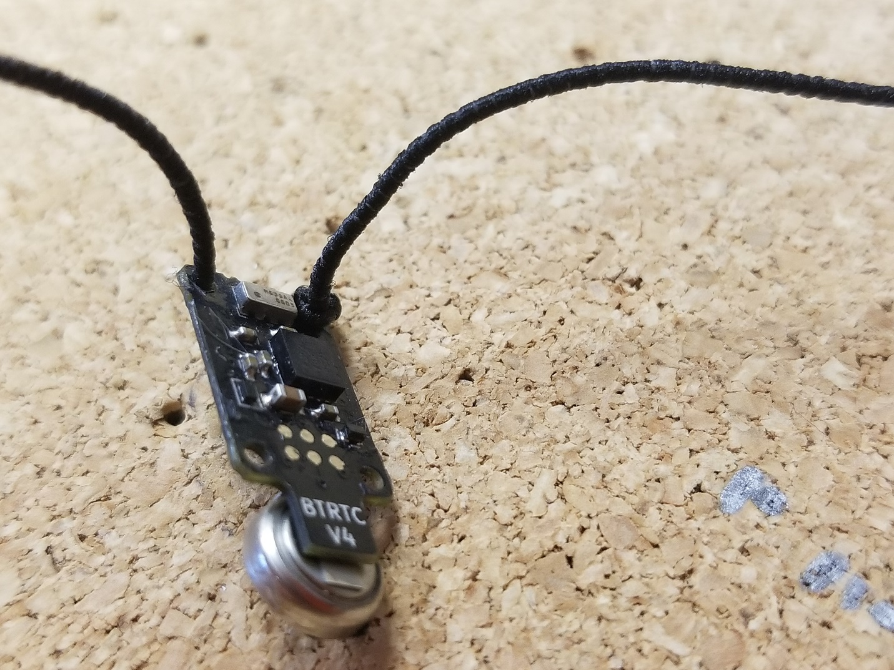
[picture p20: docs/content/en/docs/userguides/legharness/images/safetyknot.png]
Safety Knot

<figcaption align=center>Fig. 3 Safety Knot </figcaption>
</figure>

{{< /columns >}}

## Step 4: Finish Threading Loops !

{{< columns >}}

Put the string through the rest of the holes so that two loops can be made.

<--->

<figure align=center>
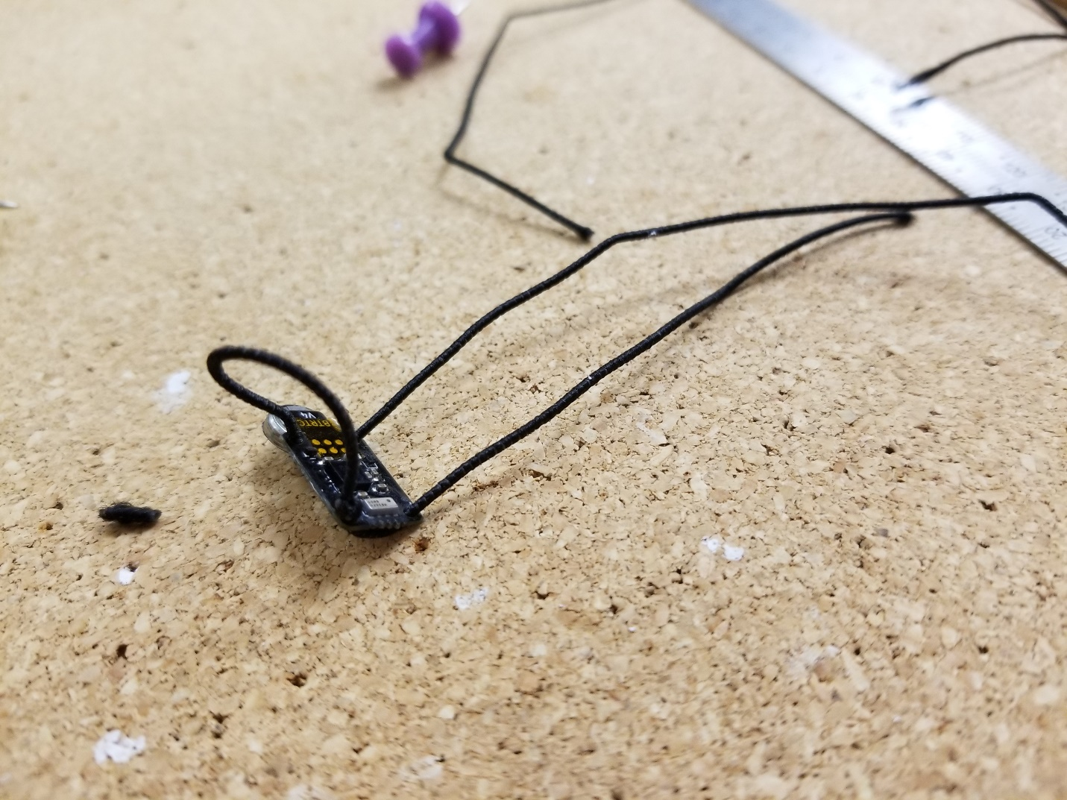
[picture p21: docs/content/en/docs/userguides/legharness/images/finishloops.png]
Finish Loops

<figcaption align=center>Fig. 4  Finish Threading Loops </figcaption>
</figure>

{{< /columns >}}

## Step 5:  Measure Your Harness

{{< columns >}}

* You should have measurements in mind before you start building a harness
* However, you will only be able to get an accurate measurement of harness size at this step
* Take two thumbtacks and place them so that their distance is your desired size
* Place the logger around the two thumbtacks; here it measured below for about 43 mm
* It’s important to note that the logger is not holding itself together yet! The untied portion is being held taught to estimate the desired size.

<--->

<figure align=center>
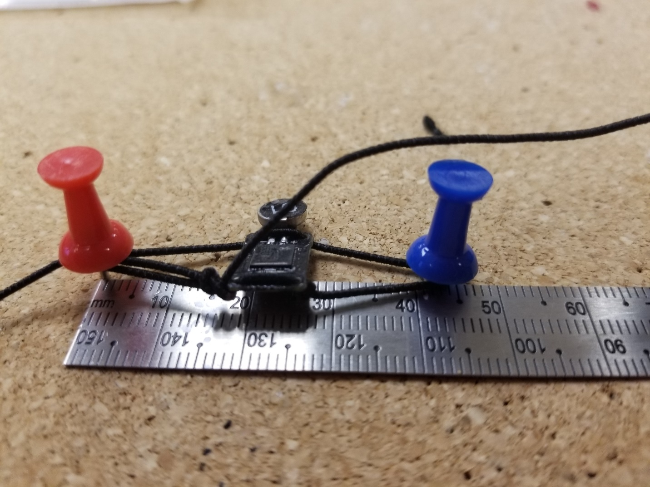
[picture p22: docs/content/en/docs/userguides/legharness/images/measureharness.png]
Measure Harness

<figcaption align=center>Fig. 5 Measuring the Harness </figcaption>
</figure>

{{< /columns >}}

## Step 6:  Mark Your String

{{< columns >}}

* Holding the harness tight, but not too tight, make a mark on the strings so that a knot may be tied on the base of the left side of the logger.
* Again, make sure not to have the string too tight (if the thumbtacks are being pulled off the board, it’s too tight.)

<--->

<figure align=center>
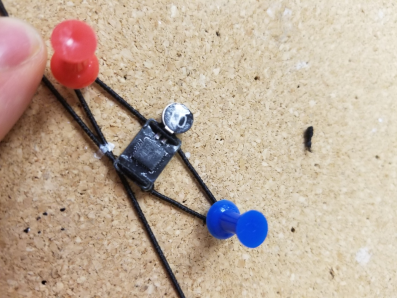
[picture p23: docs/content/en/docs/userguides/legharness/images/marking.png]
Marking the Harness

<figcaption align=center>Fig. 6 Marking the Harness</figcaption>
</figure>

{{< /columns >}}

## Step 7: Tying Off

{{< columns >}}

* Use the white marks to line up the knot to the size you had measured (there will be some estimation involved but you can always refer to your tacks).
* The knots should be tied so that they will stay at the base of the logger (notice the tape, that will need to be applied over the gold dots after charging)
* Make sure to check your size, once you have tightened the knot and cut the extra strings.

<--->

<figure align=center>
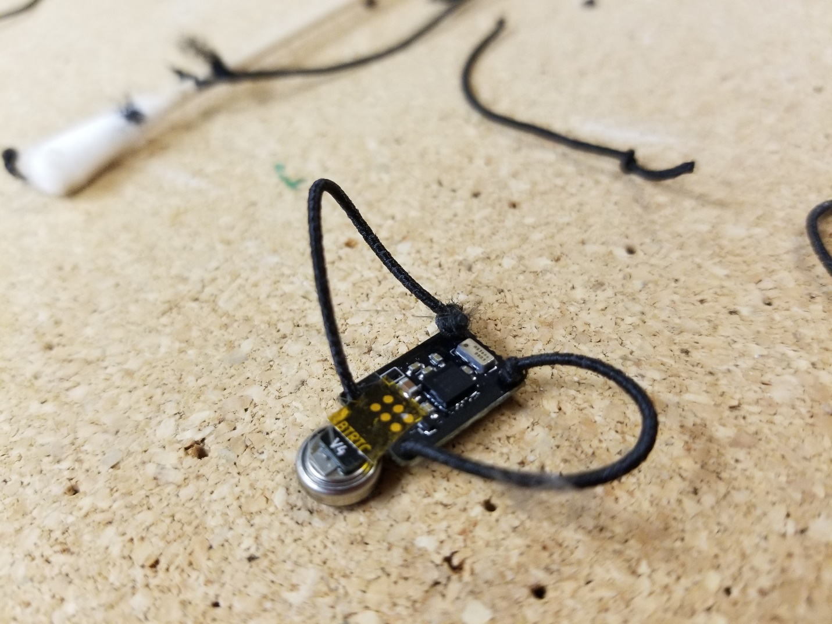
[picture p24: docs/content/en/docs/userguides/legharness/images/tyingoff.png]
Tying the Harness

<figcaption align=center>Fig. 7 Tying the Harness</figcaption>
</figure>
{{< /columns >}}

## Step 8: Sealing the Knots

{{< columns >}}
* Apply nail polish to the knots as shown so that the knots will hold.
* It will dry and function as glue (it is also optional to use super glue)
* Try not to use so much that it gets on the rest of the logger.

<--->

<figure align=center>
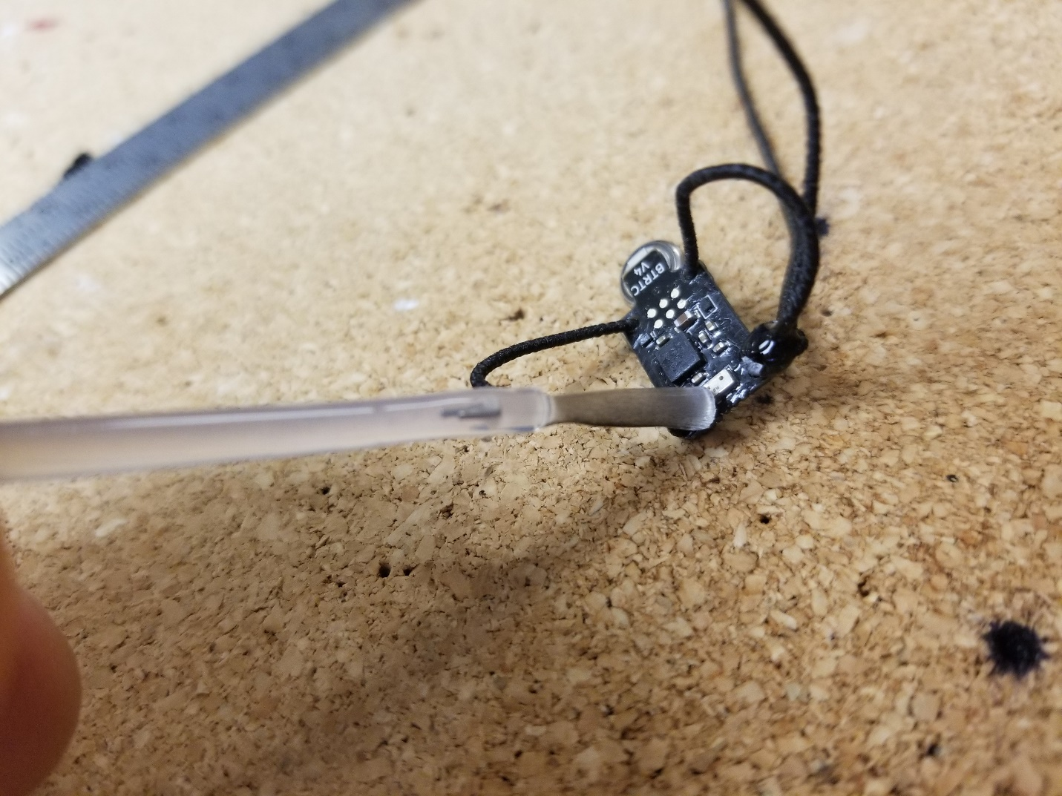
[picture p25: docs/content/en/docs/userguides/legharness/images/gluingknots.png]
Sealing the Knots

<figcaption align=center>Fig. 8 Sealing the Knots</figcaption>
</figure>

{{< /columns >}}

## Step 9: Admire Your Work

{{< columns >}}

* Congratulations! You have finished !
* You can refer to your tacks one last time to make sure that your measurements have been accurate.

<--->

<figure align=center>
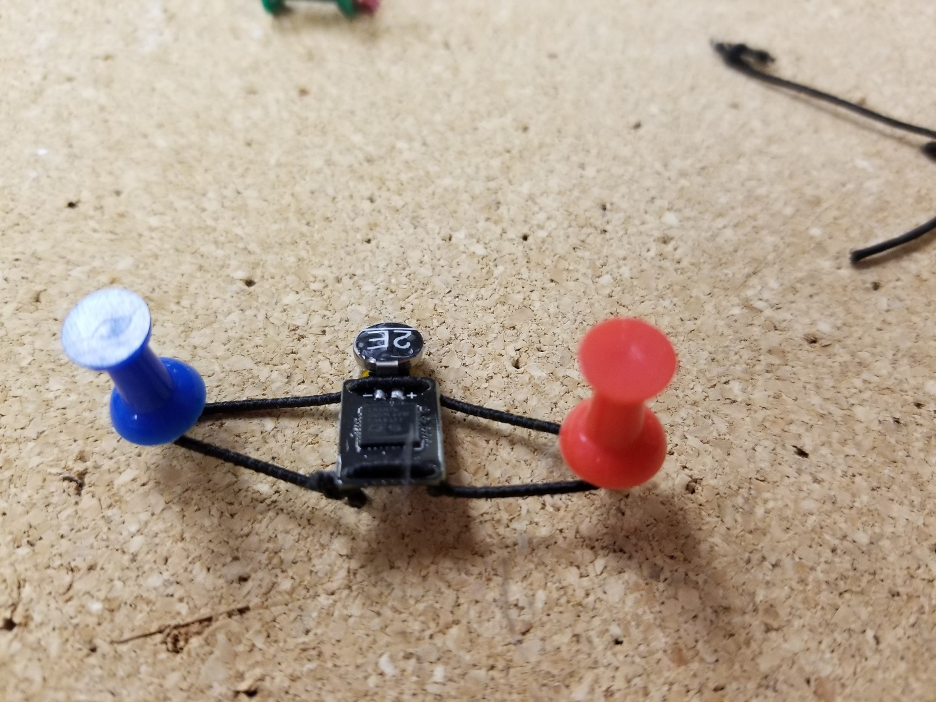
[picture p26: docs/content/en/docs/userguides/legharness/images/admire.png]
Admire Your Work

<figcaption align=center>Fig. 9 Admire Your Work</figcaption>
</figure>

{{< /columns >}}

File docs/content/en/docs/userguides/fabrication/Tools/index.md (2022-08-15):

---
title: "Tools"
description: "Tools and Supplies"
type: docs
bookToc: false 
bookCollapseSection: false
---

# Tools and Supplies 

A variety of tools and supplies are needed to 

1. Prepare tags for flight
2. Assemble tags
3. Assembly bases and chargers

Most users will be concerned only with (1)

# Preparing Tags For Flight

For a guide to preparing tags for flight see [section].  This guide, by Jiawei Chen and Tim Greives, while written for the BitTag, applies to other tags as well.

Assuming that the tags are fully assembled, the only supplies and tools required are 

<div class="clearfix">
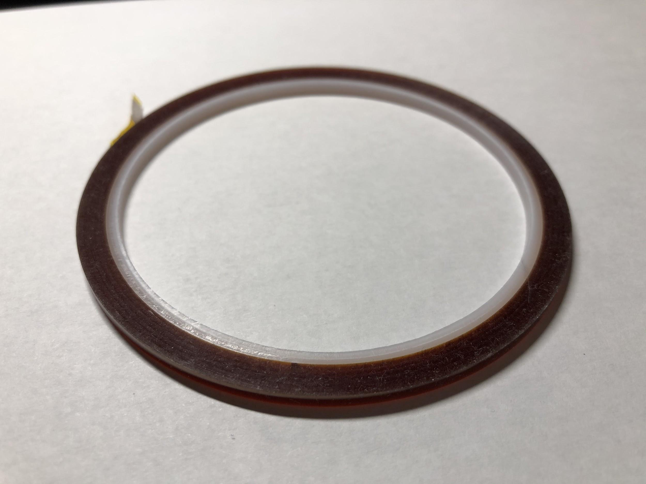
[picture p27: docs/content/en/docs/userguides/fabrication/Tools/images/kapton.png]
kapton tape


**3mm Kapton (polymide) Tape**:  Kapton tape is widely use for insulation on electronics and holds up well under challenging conditions.  For tag flight preparation, a rectangle 3mm by 4mm is ideal for covering the test points on a tag used by the base and chargers for communication.
</div>

<div class="clearfix">
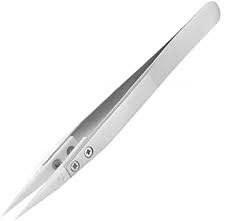
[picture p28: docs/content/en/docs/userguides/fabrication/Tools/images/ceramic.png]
ceramic tweezers


**Ceramic Tweezers**:  While not strictly necessary, ceramic
tweezers are ideal for manipulating the small rectangles of tape used to insulate the tag test points.  These can be obtained inexpensively from Amazon.
</div>

<div class="clearfix">
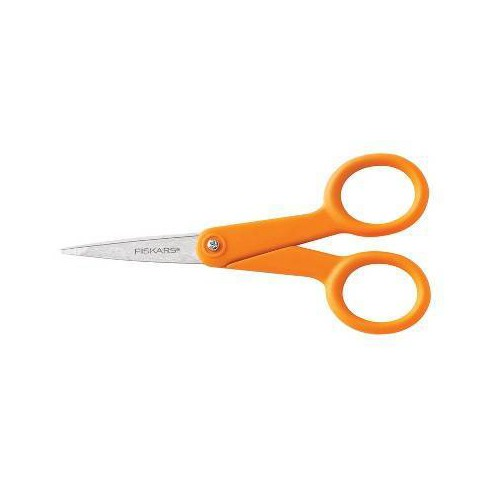
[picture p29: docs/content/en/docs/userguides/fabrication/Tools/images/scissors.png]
scissors


**Small Scissors**:  A pair of small, sharp scissors is essential for tag preparation.
</div>

<div class="clearfix">

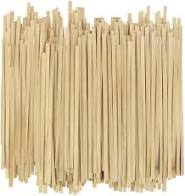
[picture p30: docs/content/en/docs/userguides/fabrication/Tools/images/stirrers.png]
coffee stirrers

**Tape Application Sticks** (4mm wooden coffee stirrers)
Wooden coffee stirrers are ideal for smoothing insulating tape while minimizing the potential for damage.

</div>

<div class="clearfix">
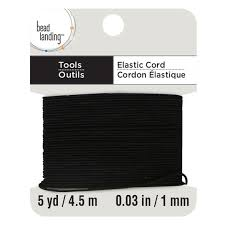
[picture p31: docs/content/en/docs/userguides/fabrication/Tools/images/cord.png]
elastic cord


**Harness Material (elastic cord)**  1mm (or smaller) 
elastic cord is needed for building harnesses.  See
[leg harness section](/docs/userguides/legharness) for directions.

</div>

# Assembling Tags

The process of assembling tags includes soldering on batteries and applying insulation.  There are two types of insulation used -- the batteries are covered in 1mil kapton tape and, after soldering, the entire assembly is dipped into a urethane coating.

<div class="clearfix">
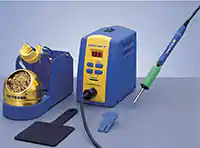
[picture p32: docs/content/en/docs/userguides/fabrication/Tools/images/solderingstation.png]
soldering station


**Soldering Station** for the fine level assembly required it essential to use a high quality temperature controlled soldering iron with a fine-pitched tip.  In our lab we use the Hakko FX-951 soldering station with fine conical tips (e.g. 0.2mm T15-IL) for most work
</div>

<div class="clearfix">
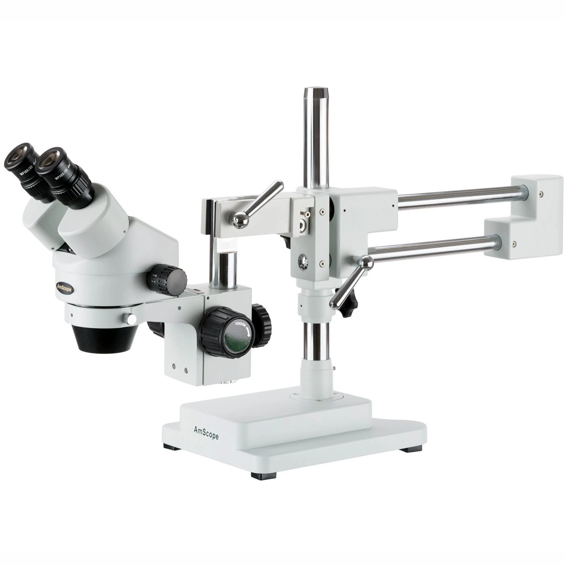
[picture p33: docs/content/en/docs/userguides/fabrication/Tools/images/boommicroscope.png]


**Boom Microscope**  A microscope is not required for assembling tags, but is definitely helpful.  Ideally, this should be a microscope with zoom capability.

</div>

<div class="clearfix">
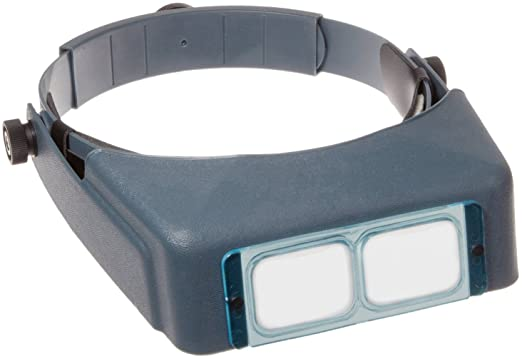
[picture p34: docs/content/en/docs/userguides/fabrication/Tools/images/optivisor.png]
optivisor


**Optivisor** An optivisor is essential for the fine work necessary to assemble tags.  Be careful to request the ones with glass lenses !
</div>

<div class="clearfix">
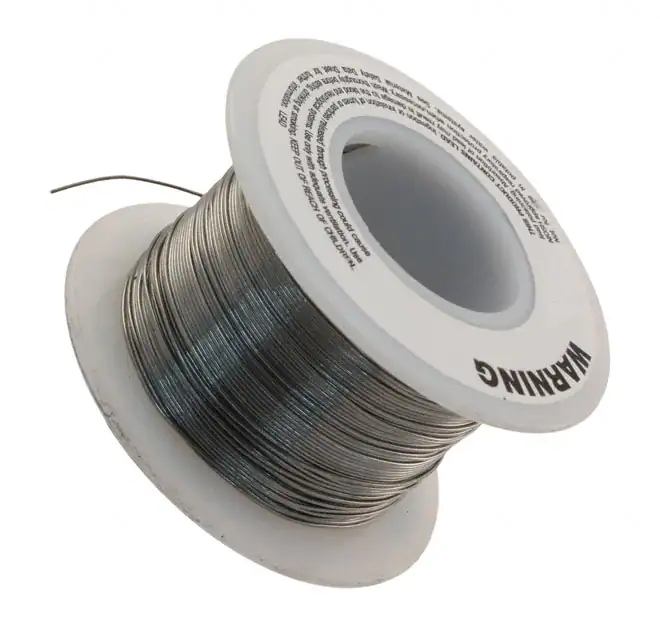
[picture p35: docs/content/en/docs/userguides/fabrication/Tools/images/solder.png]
solder


**Solder** A small diameter (e.g. 0.02 inch), leaded, flux core solder is essential.

</div>

<div class="clearfix">
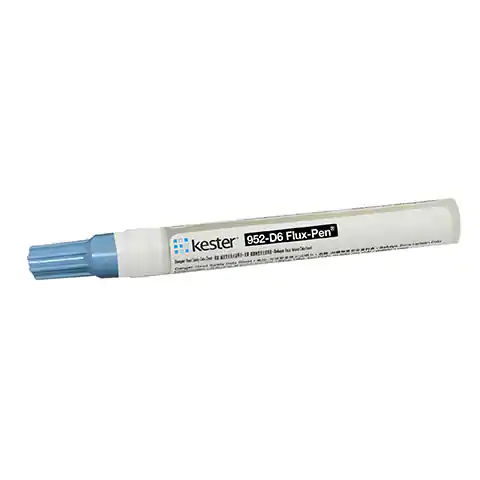
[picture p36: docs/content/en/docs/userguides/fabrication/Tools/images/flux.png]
flux


**Flux** in pen form is especially useful for soldering small components such as batteries.
</div>

<div class="clearfix">
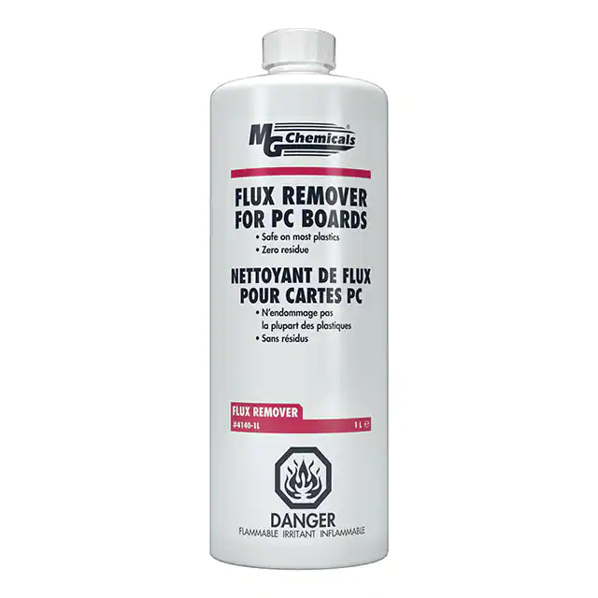
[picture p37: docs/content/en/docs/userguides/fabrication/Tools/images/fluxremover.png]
flux remover


** Flux Remover** After soldering, all components should be carefully cleaned with flux remover. 

</div>

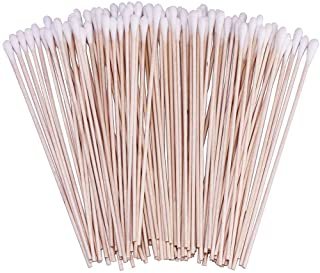
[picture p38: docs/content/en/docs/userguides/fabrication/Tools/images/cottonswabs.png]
cotton swabs
<div  class="clearfix"> 

**Cotton Swabs** We use fine cotton swabs for this purpose.
</div>

<div class="clearfix">

**Kapton Tape**  Various widths of 1mil kapton tape are required for wrapping batteries (1/4", 3/8", 1/2") depending upon battery diameter.  Ideally the tape should be slightly wider than the battery.
</div>

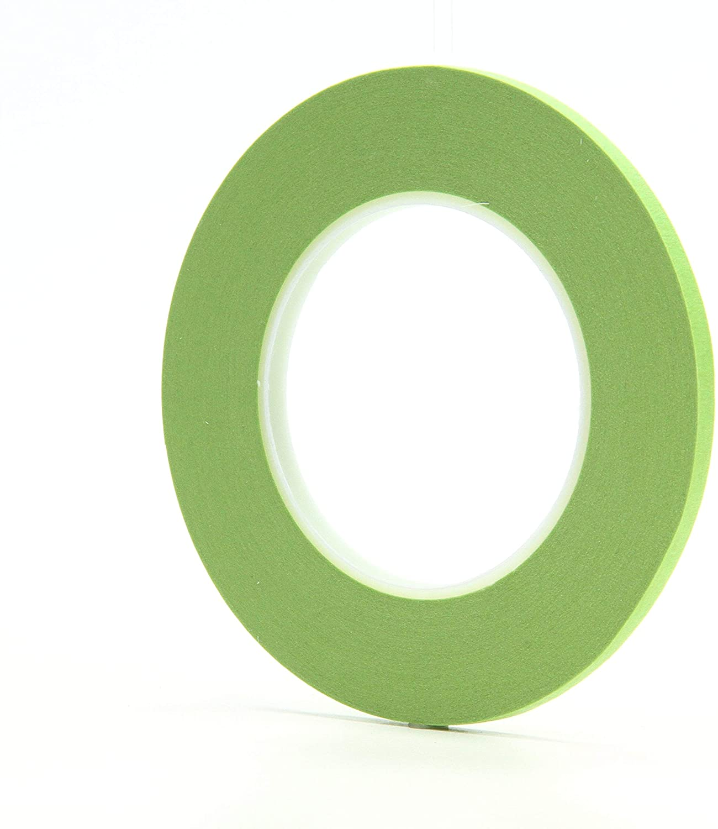
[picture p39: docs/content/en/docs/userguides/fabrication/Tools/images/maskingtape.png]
Masking Tape
<div  class="clearfix">

**Masking Taper**  During the coating process we use 6mm Scotch Masking Tape 233 to protect the contacts from the coating.  This is an automotive paint masking tape that bonds well, removes easily, and is compatible with various solvents.

</div>

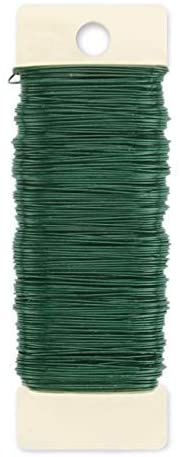
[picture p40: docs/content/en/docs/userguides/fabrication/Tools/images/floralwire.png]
FLoral Wire
<div  class="clearfix">

**Floral Wire**  We use 24 gauge floral wire to make disposable hangers for the tags for use during the coating process.  This is soft, easily bendable wire.

</div>

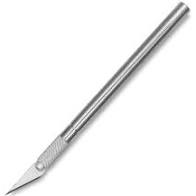
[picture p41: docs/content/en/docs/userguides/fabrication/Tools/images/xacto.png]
xacto knife
<div  class="clearfix">

**xacto knife** An x-acto #1 is essential for cleaning excess coating material after coating tags.

</div>

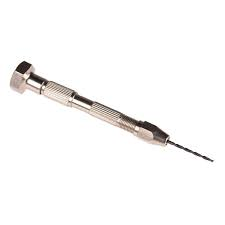
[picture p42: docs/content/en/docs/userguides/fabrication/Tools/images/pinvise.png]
pin vise
<div  class="clearfix">

**Pin Vise**  A pin vise with 1-1.1 mm drill is needed for cleaning the tag holes after coating
</div>

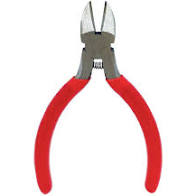
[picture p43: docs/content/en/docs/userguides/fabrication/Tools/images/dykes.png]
diagonal cutters
<div  class="clearfix">

**Diagonal Cutters** A small pair of diagonal cutters is needed for forming the tag hangers for coating.
</div>

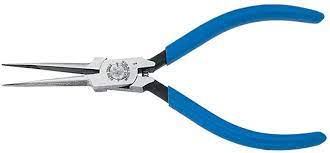
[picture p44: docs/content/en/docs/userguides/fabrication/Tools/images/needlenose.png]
needle nose pliers
<div  class="clearfix">

**Needle Nose Pliers**  A small pair of needle nose pliers is needed for forming hangers.
</div>

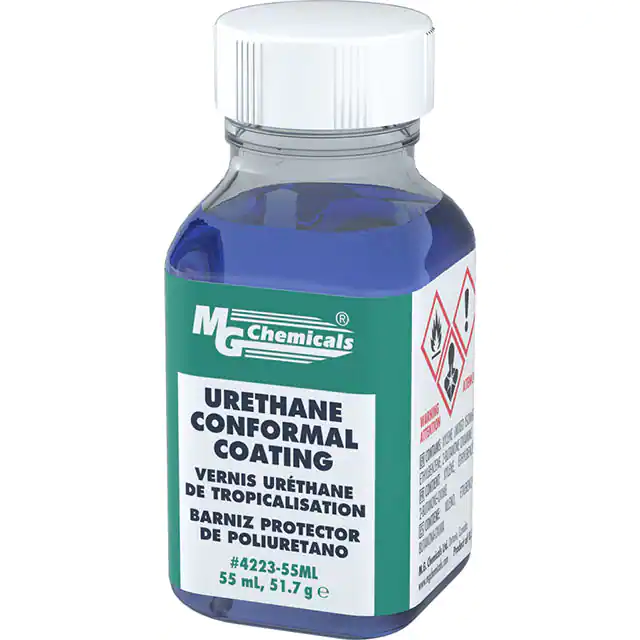
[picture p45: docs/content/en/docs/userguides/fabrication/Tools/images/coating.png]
Urethane Coating
<div  class="clearfix">

**MG 4223** We use MG Chemicals 4223 urethane coating for insulating the tags. This is available in a 55ml bottle. In practice we immerse the tags (with batteries) directly in the coating and hang them to dry.

</div>

# Assembly of Bases and Chargers

The assembly of bases and chargers requires the soldering tools described above (soldering station, microscope, solder, flux, flux remover).  In addition it is helpful to have tools to hold the various boards during assembly.

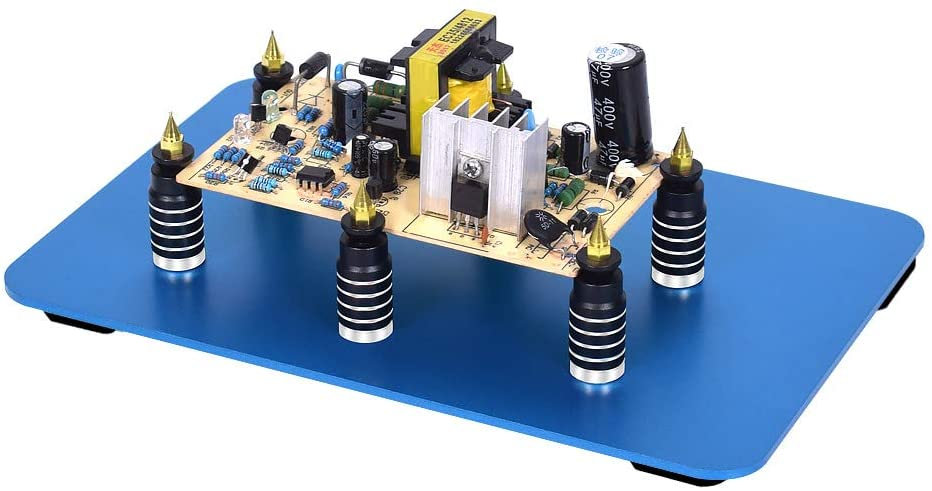
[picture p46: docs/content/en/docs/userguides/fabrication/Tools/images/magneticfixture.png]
Magnetic Fixture
<div  class="clearfix">

**Toolour magnetic fixture tower** Magnetic fixtures such as this are useful for holding boards during soldering

</div>

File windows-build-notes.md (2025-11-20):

cmake -B build -S  c:/users/geobrown/ultralight-tags --preset default
cmake --build . --config Release

qt-cmake -G "MinGW Makefiles" -DVCPKG_TARGET_TRIPLET="x64-mingw-static" -DCMAKE_TOOLCHAIN_FILE="d:/vcpkg/scripts/buildsystems/vcpkg.cmake"  c:/users/geobrown/ultralight-tags

Protobuf_DIR=d:/vcpkg/installed/x64-mingw-static/tools/protobuf
mac:

Note: compiling embedded software on windows is broken because of the use of "cat" in chibios make files

Install -
* chocolaty [must run in admin powershell]
    * choco install make
    * choco install pkgconfiglites

* Environment Variables
    * NANOPB_ROOT C:\users\geobrown\nanopb
    * VCPKG_ROOT  D:\vcpkg  --- skip, use builtin vcpkg
    * VCPKG_DEFAULT_TRIPLET x64-windows-static
    * STM32_PRG_PATH  C:\Program Files (x86)\STMicroelectronics\STM32Cube\STM32CubeProgrammer\bin
    * CHIBIOS_DIR D:\ChibiOS

* Path additions
    * D:\vcpkg
    * C:\Program Files (x86)\Arm GNU Toolchain arm-none-eabi\14.2 rel1\bin
    * c:\users\geobrown\fmpp\bin
    * D:\Qt\x64-static\bin
    * C:\ProgramData\chocolatey\bin

--- To build ultralight tools on windows --

see [qt path bug](https://bugreports.qt.io/browse/QTBUG-97615)

cmake -G "Visual Studio 17 2022" -Ax64 -DVCPKG_TARGET_TRIPLET="x64-windows-static" --preset=default -DQt6_DIR="d:/Qt/x64-static" -DQT_ADDITIONAL_PACKAGES_PREFIX_PATH="d:/Qt/x64-static"

Build -- 
* QT x64-windows-static

links - [Install with cmake](https://learn.microsoft.com/en-us/vcpkg/get_started/get-started?pivots=shell-powershell
)

```
cd D:\qt-build
cmd /E:ON /V:ON /k C:\Users\geobrown\qtvars.cmd
```

```
C:\Qt\6.8.2\src\configure.bat -static -debug-and-release -opensource -static-runtime -skip qt3d -skip qtactiveqt -skip qtandroidextras -skip qtcharts -skip qtconnectivity -skip qtdatavis3d -skip qtdeclarative -skip qtdoc -skip qtgamepad -skip qtlocation -skip qtlottie -skip qtmacextras -skip qtmultimedia -skip qtnetworkauth -skip qtpurchasing -skip qtquick3d -skip qtquickcontrols -skip qtquickcontrols2 -skip qtquicktimeline -skip qtremoteobjects -skip qtscript -skip qtsensors -skip qtspeech -skip qtsvg -skip qtwayland -skip qtwebglplugin -skip qtwebview -skip webengine -nomake examples -nomake tests -skip qtgraphs -skip qtmqtt -skip qtopcua -skip qt3d -skip qtquick3dphysics -skip qtquickeffectmaker -skip qtvirtualkeyboard -skip qtwebchannel -skip qtwebsockets -skip qtcoap -skip qtgrpc -skip qthttpserver -prefix d:/Qt/x64-static

```

```
in the build directory do this:

D:\Qt\src\configure.bat -static -debug-and-release -opensource -static-runtime -platform win32-msvc -nomake examples -nomake tests -prefix d:/Qt/x64-static
cmake --build .
cmake -DCMAKE_INSTALL_PREFIX=d:/Qt/x64-static install .

or

D:\Qt\src\configure.bat -static -debug-and-release -opensource -static-runtime -platform win32-g++ -nomake examples -nomake tests -prefix d:/Qt/x64-mingw-static
cmake --build .
cmake -DCMAKE_INSTALL_PREFIX=d:/Qt/x64-static install .
```

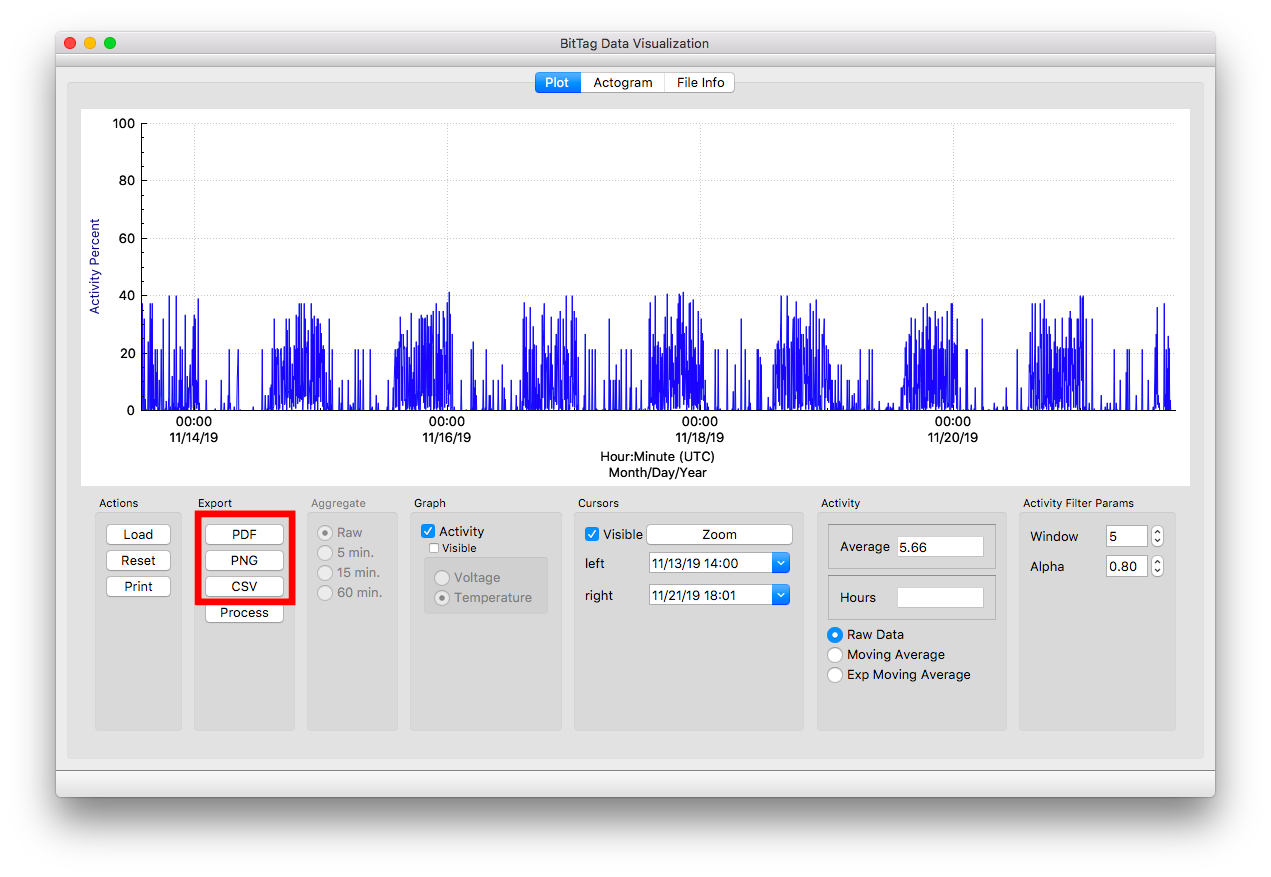
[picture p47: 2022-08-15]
docs/content/en/docs/userguides/preflight/images/image32.png

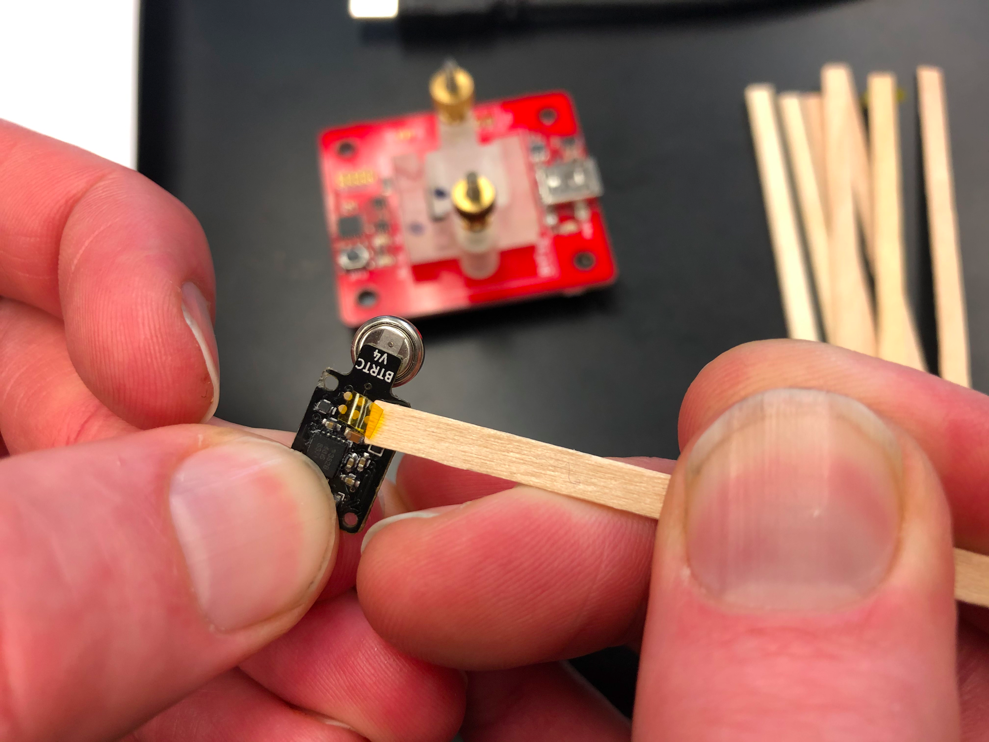
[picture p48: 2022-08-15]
docs/content/en/docs/userguides/preflight/images/image45.png

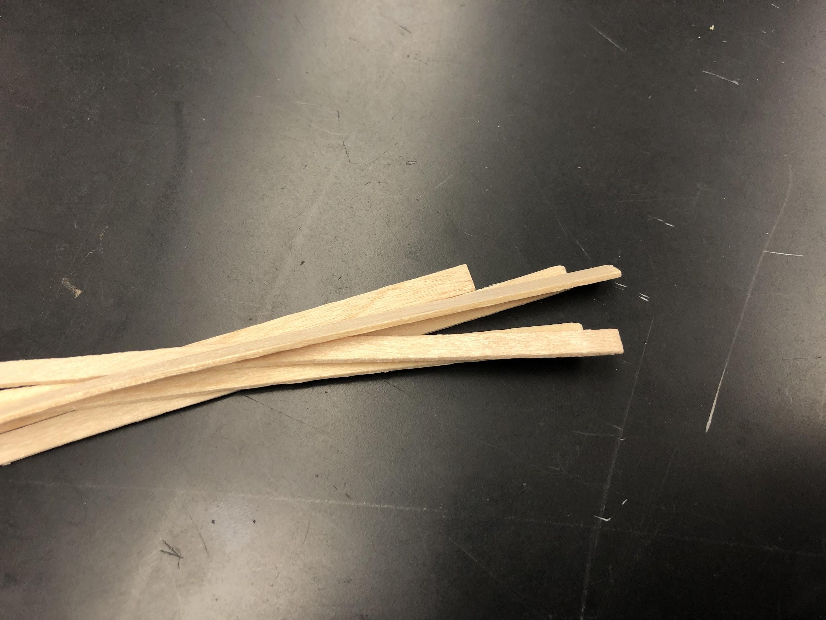
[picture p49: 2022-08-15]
docs/content/en/docs/userguides/preflight/images/image23.jpg

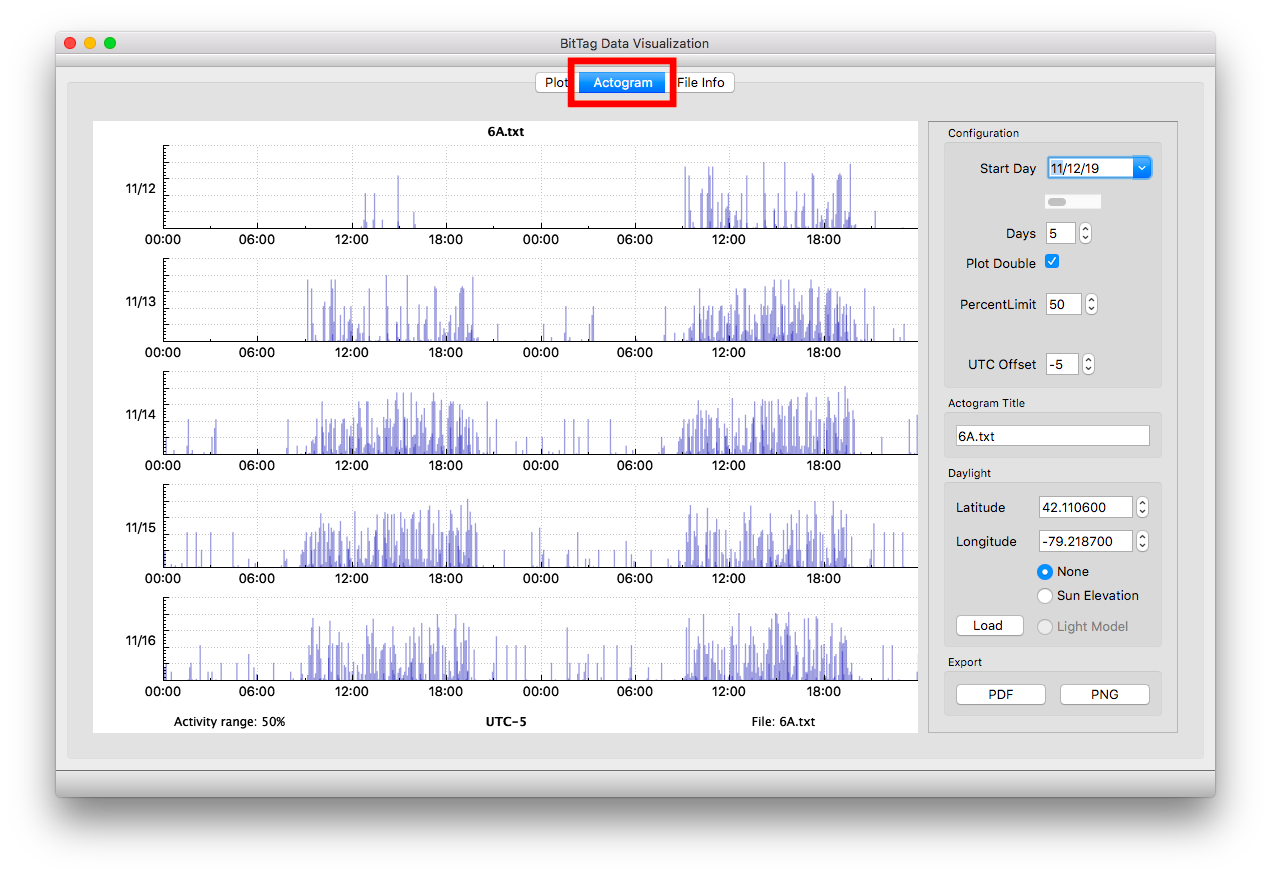
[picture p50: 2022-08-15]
docs/content/en/docs/userguides/preflight/images/image10.png

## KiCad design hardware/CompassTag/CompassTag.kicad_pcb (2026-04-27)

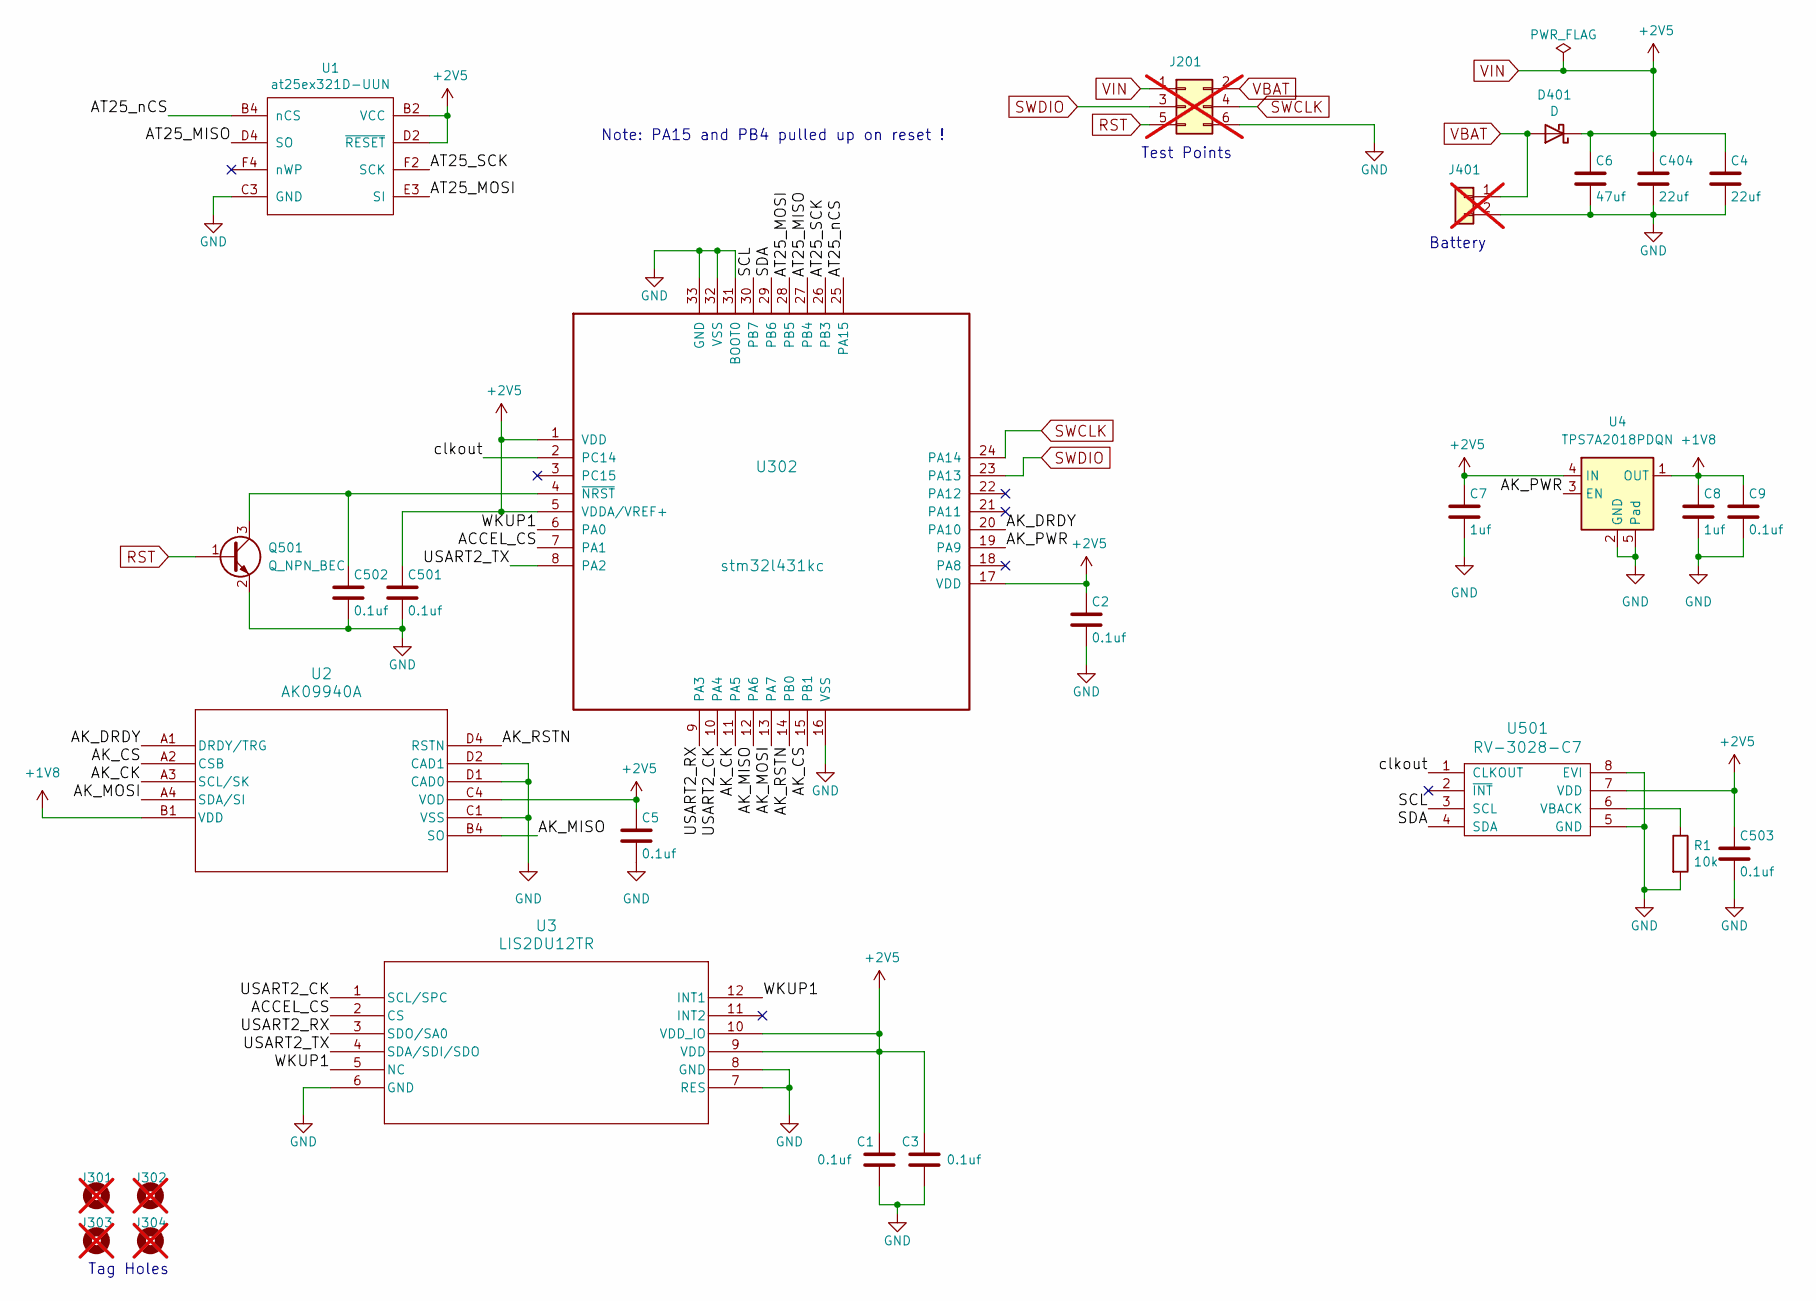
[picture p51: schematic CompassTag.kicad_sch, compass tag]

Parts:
C1, C2, C3, C5, C9, C501, C502, C503: 0.1uf; C_0201_0603Metric; MPN GRM033R60J105MEA2D; LCSC C181047
C4, C404: 22uf; C_0402_1005Metric; MPN 04026D226MAT2A; LCSC C2179118
C6: 47uf; C_0603_1608Metric; MPN 06036D476MAT2A
C7, C8: 1uf; C_0201_0603Metric; MPN GRT033R60J105ME13D
D401: D; D_0402_1005Metric; MPN CDBQC0130L-HF; LCSC C2886012
J201: CONN_02X04; tagpoints6; not fitted
J301, J302, J303, J304: Conn_01x01; taghole1.1mm; not fitted
J401: CONN_01X02; MS621; not fitted
Q501: Q_NPN_BEC; SOT-883; MPN BC847AMB,315; LCSC C686658
R1: 10k; R_0201_0603Metric; MPN RC0201FR-0710KL; LCSC C106225
U1: at25ex321D-UUN; adesto_wlcsp12; MPN AT25XE321D-UUN-T; LCSC C1858339
U2: AK09940A; LGA11_1p6x1p6x0p58_AKM; MPN AK09940A
U3: LIS2DU12TR; LGA-12L_LIS2DU12_STM; MPN LIS2DU12TR
U4: TPS7A2018PDQN; Texas_X2SON-4_1x1mm_P0.65mm; MPN TPS7A2018PDQNR
U302: stm32l431kc; QFN-32-1EP_5x5mm_P0.5mm_EP3.45x3.45mm; MPN STM32L432KCU6; LCSC C1337280
U501: RV-3028-C7; RV-8803-C7; MPN RV-3028-C7 32.768KHZ 1PPM-TA-QA; LCSC C3019759

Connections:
+1V8: C8.1, C9.1, U2.B1 (VDD), U4.1 (OUT)
/ACCEL_CS: U3.2 (CS), U302.7 (PA1)
/AK_CK: U2.A3 (SCL/SK), U302.11 (PA5)
/AK_CS: U2.A2 (CSB), U302.15 (PB1)
/AK_DRDY: U2.A1 (DRDY/TRG), U302.20 (PA10)
/AK_MISO: U2.B4 (SO), U302.12 (PA6)
/AK_MOSI: U2.A4 (SDA/SI), U302.13 (PA7)
/AK_PWR: U4.3 (EN), U302.19 (PA9)
/AK_RSTN: U2.D4 (RSTN), U302.14 (PB0)
/AT25_MISO: U1.D4 (SO), U302.27 (PB4)
/AT25_MOSI: U1.E3 (SI), U302.28 (PB5)
/AT25_SCK: U1.F2 (SCK), U302.26 (PB3)
/AT25_nCS: U1.B4 (nCS), U302.25 (PA15)
/SCL: U302.30 (PB7), U501.3 (SCL)
/SDA: U302.29 (PB6), U501.4 (SDA)
/USART2_CK: U3.1 (SCL/SPC), U302.10 (PA4)
/USART2_RX: U3.3 (SDO/SA0), U302.9 (PA3)
/USART2_TX: U3.4 (SDA/SDI/SDO), U302.8 (PA2)
/WKUP1: U3.5 (NC), U3.12 (INT1), U302.6 (PA0)
/clkout: U302.2 (PC14), U501.1 (CLKOUT)
GND: C1.2, C2.2, C3.2, C4.2, C5.2, C6.2, C7.2, C8.2, C9.2, C404.2, C501.2, C502.2, C503.2, J201.6, J401.2, Q501.2 (E), R1.2, U1.C3 (GND), U2.C1 (VSS), U2.D1 (CAD0), U2.D2 (CAD1), U3.6 (GND), U3.7 (RES), U3.8 (GND), U4.2 (GND), U4.5 (Pad), U302.16 (VSS), U302.31 (BOOT0), U302.32 (VSS), U302.33 (GND), U501.5 (GND), U501.8 (EVI)
unnamed: C502.1, Q501.3 (C), U302.4 (~NRST)
unnamed: R1.1, U501.6 (VBACK)
RST: J201.5, Q501.1 (B)
SWCLK: J201.4, U302.24 (PA14)
SWDIO: J201.3, U302.23 (PA13)
VBAT: D401.2 (A), J201.2, J401.1
VIN: C1.1, C2.1, C3.1, C4.1, C5.1, C6.1, C7.1, C404.1, C501.1, C503.1, D401.1 (K), J201.1, U1.B2 (VCC), U1.D2 (~RESET), U2.C4 (VOD), U3.9 (VDD), U3.10 (VDD_IO), U4.4 (IN), U302.1 (VDD), U302.5 (VDDA/VREF+), U302.17 (VDD), U501.7 (VDD)

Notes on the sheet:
Note: PA15 and PB4 pulled up on reset !
Tag Holes
Test Points
Battery

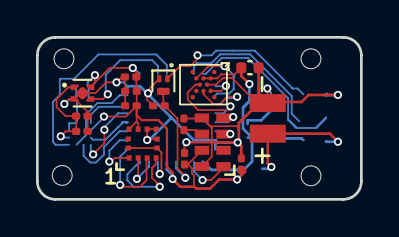
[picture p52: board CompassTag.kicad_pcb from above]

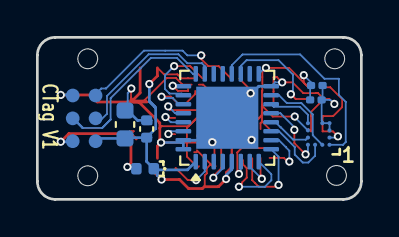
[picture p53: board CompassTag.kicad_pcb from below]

Board: 2 copper layers, 18.0 x 9.0 mm, 28 parts (8 on the bottom side), 28 nets.

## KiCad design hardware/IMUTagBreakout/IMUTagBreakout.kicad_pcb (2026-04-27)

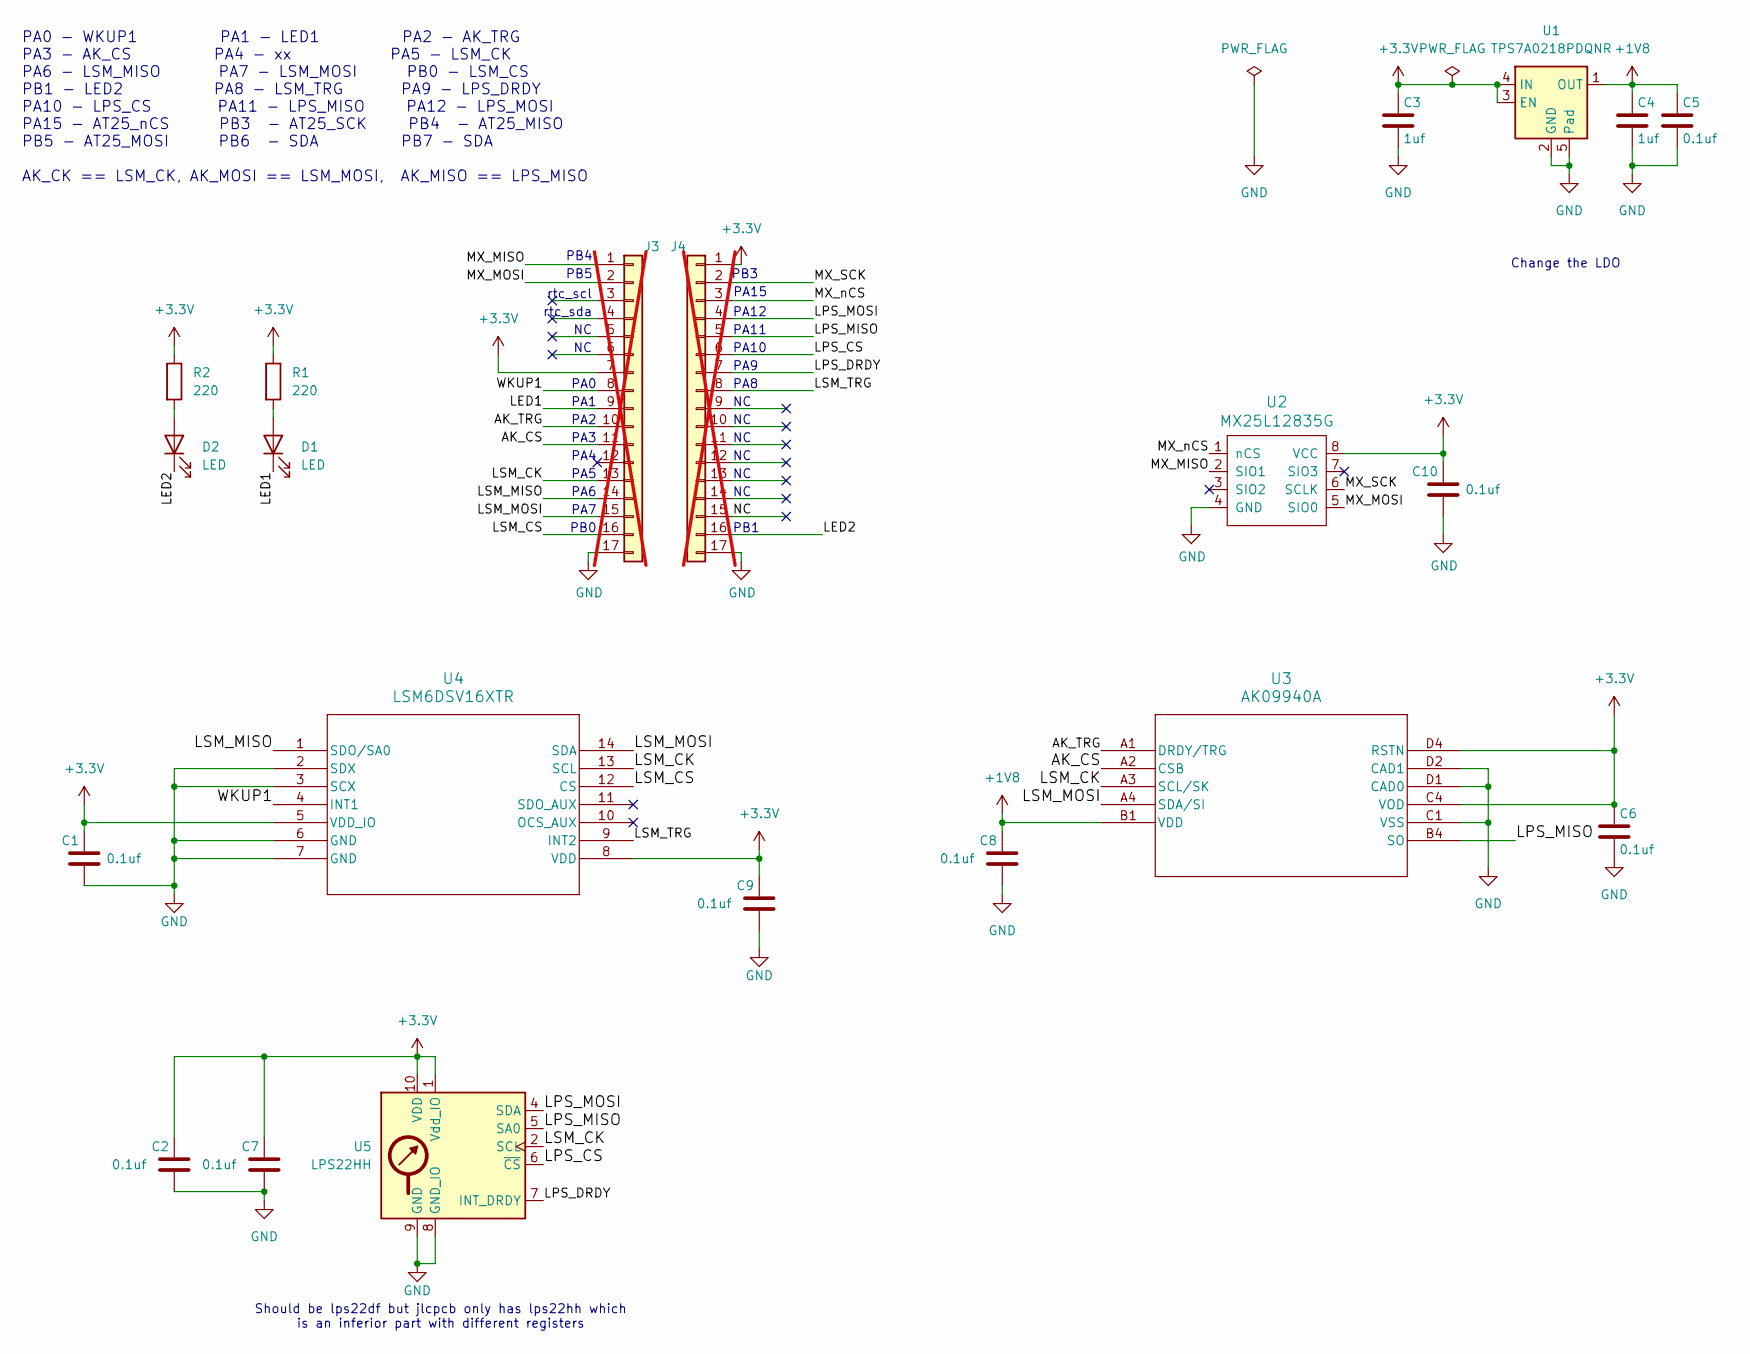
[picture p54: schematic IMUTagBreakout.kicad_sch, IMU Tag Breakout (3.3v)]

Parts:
C1, C2, C5, C6, C7, C8, C9, C10: 0.1uf; C_0603_1608Metric; MPN CC0603KRX7R9BB104; LCSC C14663
C3, C4: 1uf; C_0603_1608Metric; MPN CL10A105KB8NNNC; LCSC C15849
D1, D2: LED; LED_0603_1608Metric; MPN KT-0603R; LCSC C2286
J3, J4: Conn_01x17; PinHeader_1x17_P2.54mm_Vertical_Staggered; not fitted
R1, R2: 220; R_0603_1608Metric; MPN 0603WAF2200T5E; LCSC C22962
U1: TPS7A0218PDQNR; Texas_X2SON-4_1x1mm_P0.65mm; MPN TPS7A0218PDQNR; LCSC C2862166
U2: MX25L12835G; SOIC-8_5.3x6.2mm_P1.27mm; MPN MX25L12845GM2I-08G-TR; LCSC C136615
U3: AK09940A; AK09940a; MPN AK09940A; LCSC C6794828
U4: LSM6DSV16XTR; LGA-14_3x2.5mm_P0.5mm_LayoutBorder3x4y; MPN LSM6DSV; LCSC C5267406
U5: LPS22HH; ST_HLGA-10_2x2mm_P0.5mm_LayoutBorder3x2y; MPN LPS22HH; LCSC C2827824

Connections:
+1V8: C4.1, C5.1, C8.1, U1.1 (OUT), U3.B1 (VDD)
+3.3V: C1.1, C2.1, C3.1, C6.1, C7.1, C9.1, C10.1, J3.7, J4.1, R1.1, R2.1, U1.3 (EN), U1.4 (IN), U2.8 (VCC), U3.C4 (VOD), U3.D4 (RSTN), U4.5 (VDD_IO), U4.8 (VDD), U5.1 (Vdd_IO), U5.10 (VDD)
/AK_CS: J3.11, U3.A2 (CSB)
/AK_TRG: J3.10, U3.A1 (DRDY/TRG)
/LED1: D1.1 (K), J3.9
/LED2: D2.1 (K), J4.16
/LPS_CS: J4.6, U5.6 (~CS)
/LPS_DRDY: J4.7, U5.7 (INT_DRDY)
/LPS_MISO: J4.5, U3.B4 (SO), U5.5 (SA0)
/LPS_MOSI: J4.4, U5.4 (SDA)
/LSM_CK: J3.13, U3.A3 (SCL/SK), U4.13 (SCL), U5.2 (SCL)
/LSM_CS: J3.16, U4.12 (CS)
/LSM_MISO: J3.14, U4.1 (SDO/SA0)
/LSM_MOSI: J3.15, U3.A4 (SDA/SI), U4.14 (SDA)
/LSM_TRG: J4.8, U4.9 (INT2)
/MX_MISO: J3.1, U2.2 (SIO1)
/MX_MOSI: J3.2, U2.5 (SIO0)
/MX_SCK: J4.2, U2.6 (SCLK)
/MX_nCS: J4.3, U2.1 (nCS)
/NC: J4.15
/WKUP1: J3.8, U4.4 (INT1)
GND: C1.2, C2.2, C3.2, C4.2, C5.2, C6.2, C7.2, C8.2, C9.2, C10.2, J3.17, J4.17, U1.2 (GND), U1.5 (Pad), U2.4 (GND), U3.C1 (VSS), U3.D1 (CAD0), U3.D2 (CAD1), U4.2 (SDX), U4.3 (SCX), U4.6 (GND), U4.7 (GND), U5.3 (GND), U5.8 (GND_IO), U5.9 (GND)
unnamed: D1.2 (A), R1.2
unnamed: D2.2 (A), R2.2

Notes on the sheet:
PA1
PA9
PA2
PA0
PA8
PA7
PA15
PA5
PA4
PB3
PA6
Should be lps22df but jlcpcb only has lps22hh which is an inferior part with different registers
PA3
PB4
PA12
PB0
PA0 - WKUP1 PA1 - LED1 PA2 - AK_TRG PA3 - AK_CS PA4 - xx PA5 - LSM_CK PA6 - LSM_MISO PA7 - LSM_MOSI PB0 - LSM_CS PB1 - LED2 PA8 - LSM_TRG PA9 - LPS_DRDY PA10 - LPS_CS PA11 - LPS_MISO PA12 - LPS_MOSI PA15 - AT25_nCS PB3 - AT25_SCK PB4 - AT25_MISO PB5 - AT25_MOSI PB6 - SDA PB7 - SDA AK_CK == LSM_CK, 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
PB5
PA10
rtc_sda
PA11
PB1
rtc_scl
Change the LDO

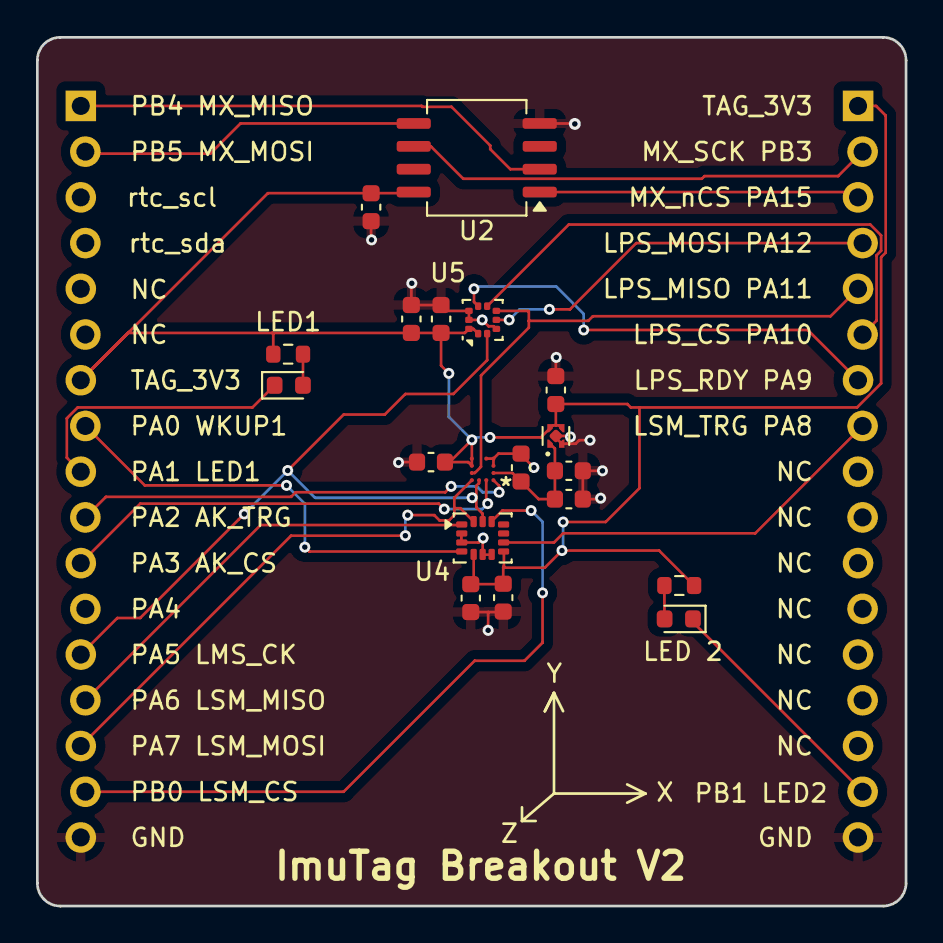
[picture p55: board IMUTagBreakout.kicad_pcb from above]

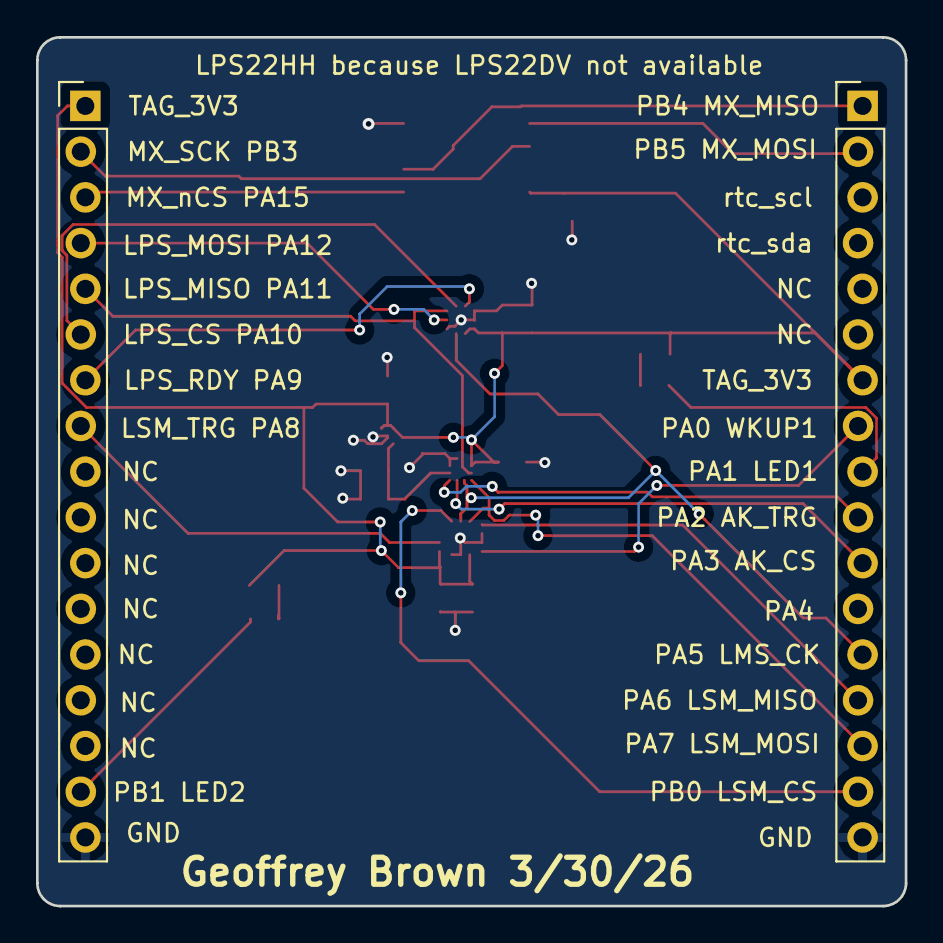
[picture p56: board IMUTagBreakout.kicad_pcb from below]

Board: 2 copper layers, 48.3 x 48.3 mm, 21 parts (2 on the bottom side), 23 nets.

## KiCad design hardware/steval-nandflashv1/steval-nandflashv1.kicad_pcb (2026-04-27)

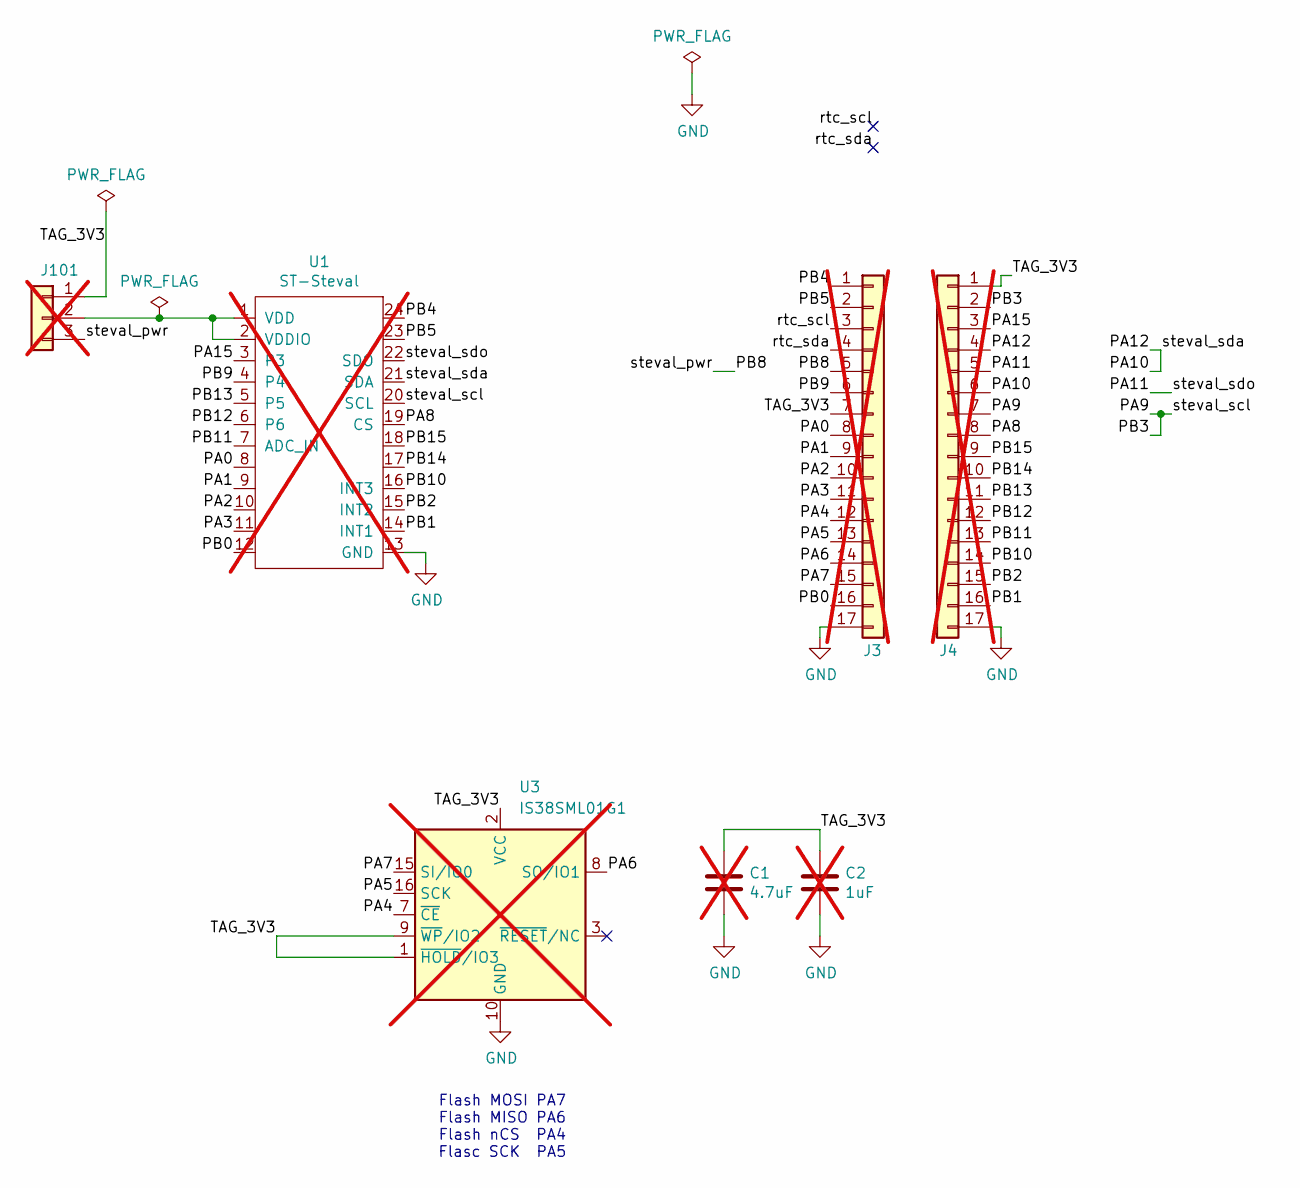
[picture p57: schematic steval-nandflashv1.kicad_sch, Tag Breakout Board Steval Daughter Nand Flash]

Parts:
C1: 4.7uF; C_0805_2012Metric; not fitted
C2: 1uF; C_0805_2012Metric; not fitted
J3, J4: Conn_01x17; PinHeader_1x17_P2.54mm_Vertical_Staggered; not fitted
J101: Conn_01x03; PinHeader_1x03_P2.54mm_Vertical; not fitted
U1: ST-Steval; DIP-24_W15.24mm_Socket; not fitted
U3: IS38SML01G1; SOIC-16W_7.5x10.3mm_P1.27mm; not fitted

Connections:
/PA0: J3.8, U1.8
/PA1: J3.9, U1.9
/PA2: J3.10, U1.10
/PA3: J3.11, U1.11
/PA4: J3.12, U3.7 (~CE)
/PA5: J3.13, U3.16 (SCK)
/PA6: J3.14, U3.8 (SO/IO1)
/PA7: J3.15, U3.15 (SI/IO0)
/PA8: J4.8, U1.19 (CS)
/PA9: J4.2, J4.7, U1.20 (SCL)
/PA10: J4.4, J4.6, U1.21 (SDA)
/PA11: J4.5, U1.22 (SDO)
/PA15: J4.3, U1.3
/PB0: J3.16, U1.12
/PB1: J4.16, U1.14 (INT1)
/PB2: J4.15, U1.15 (INT2)
/PB4: J3.1, U1.24
/PB5: J3.2, U1.23
/PB8: J3.5, J101.3
/PB9: J3.6, U1.4
/PB10: J4.14, U1.16 (INT3)
/PB11: J4.13, U1.7 (ADC_IN)
/PB12: J4.12, U1.6
/PB13: J4.11, U1.5
/PB14: J4.10, U1.17
/PB15: J4.9, U1.18
/TAG_3V3: C1.1, C2.1, J3.7, J4.1, J101.1, U3.1 (~HOLD/IO3), U3.2 (VCC), U3.9 (~WP/IO2)
/rtc_scl: J3.3
/rtc_sda: J3.4
GND: C1.2, C2.2, J3.17, J4.17, U1.13 (GND), U3.10 (GND)
unnamed: J101.2, U1.1 (VDD), U1.2 (VDDIO)

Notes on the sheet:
Flash MOSI PA7 Flash MISO PA6 Flash nCS PA4 Flasc SCK PA5

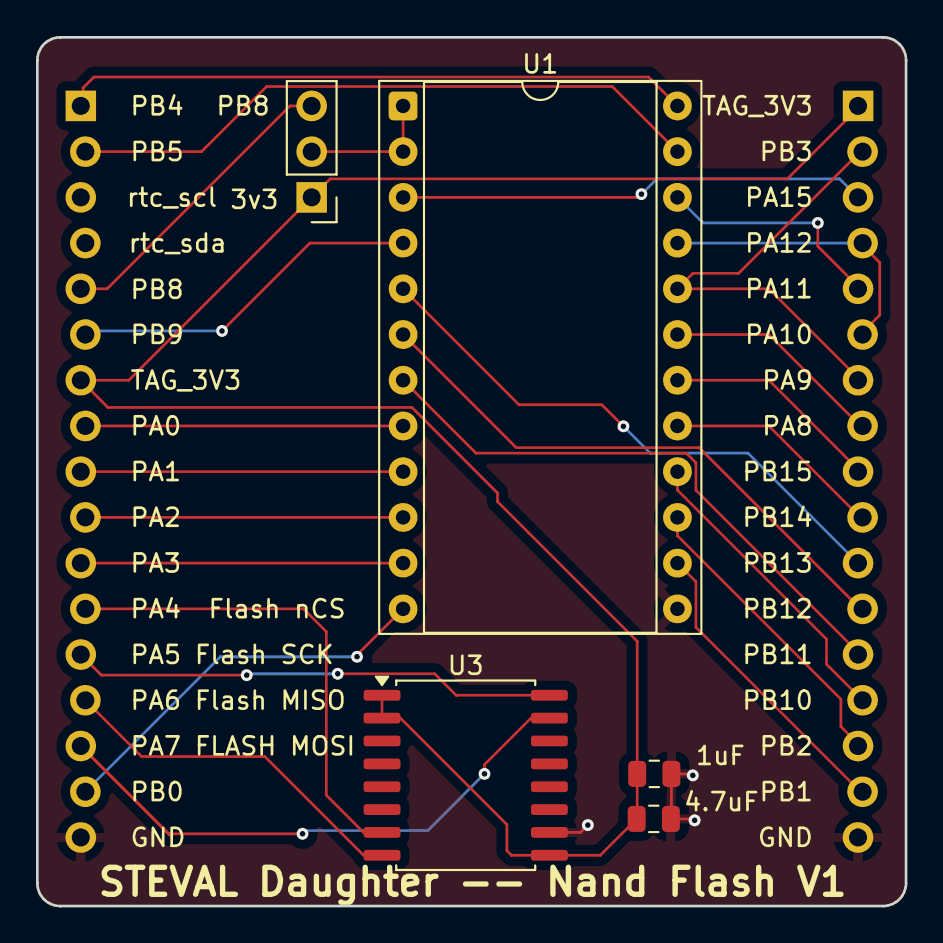
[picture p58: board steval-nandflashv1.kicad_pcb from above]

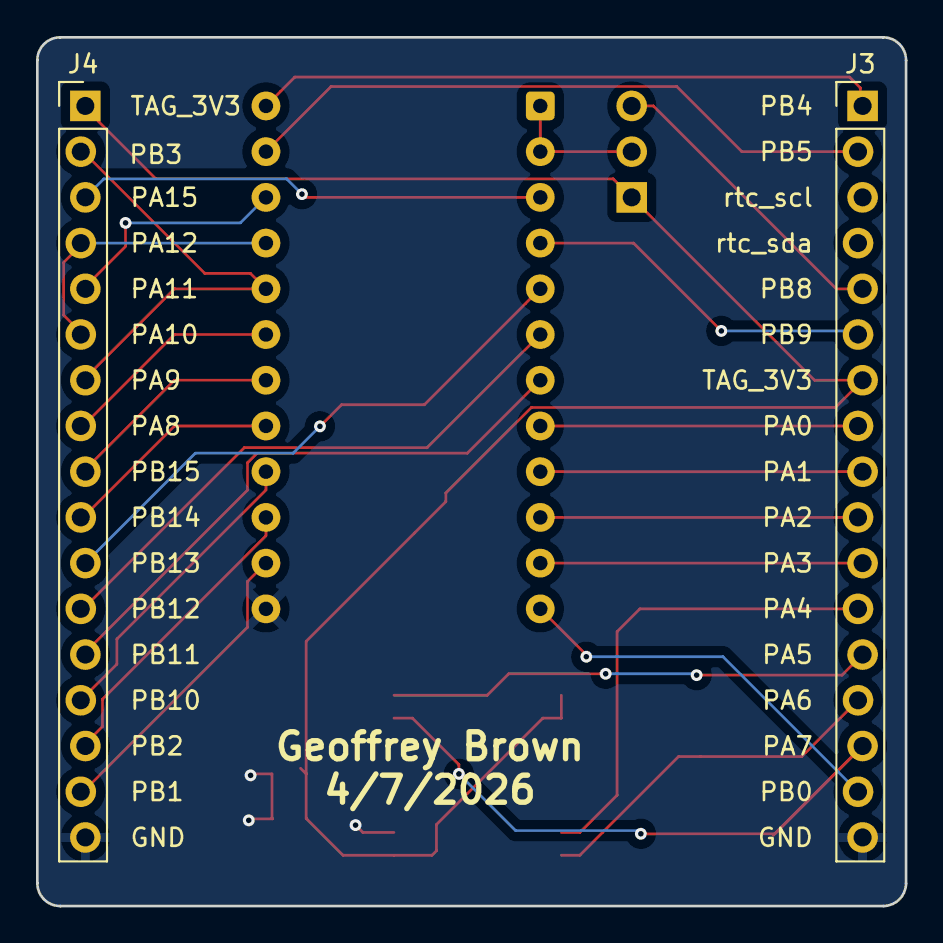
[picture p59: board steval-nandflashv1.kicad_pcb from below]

Board: 2 copper layers, 48.3 x 48.3 mm, 7 parts (2 on the bottom side), 29 nets.

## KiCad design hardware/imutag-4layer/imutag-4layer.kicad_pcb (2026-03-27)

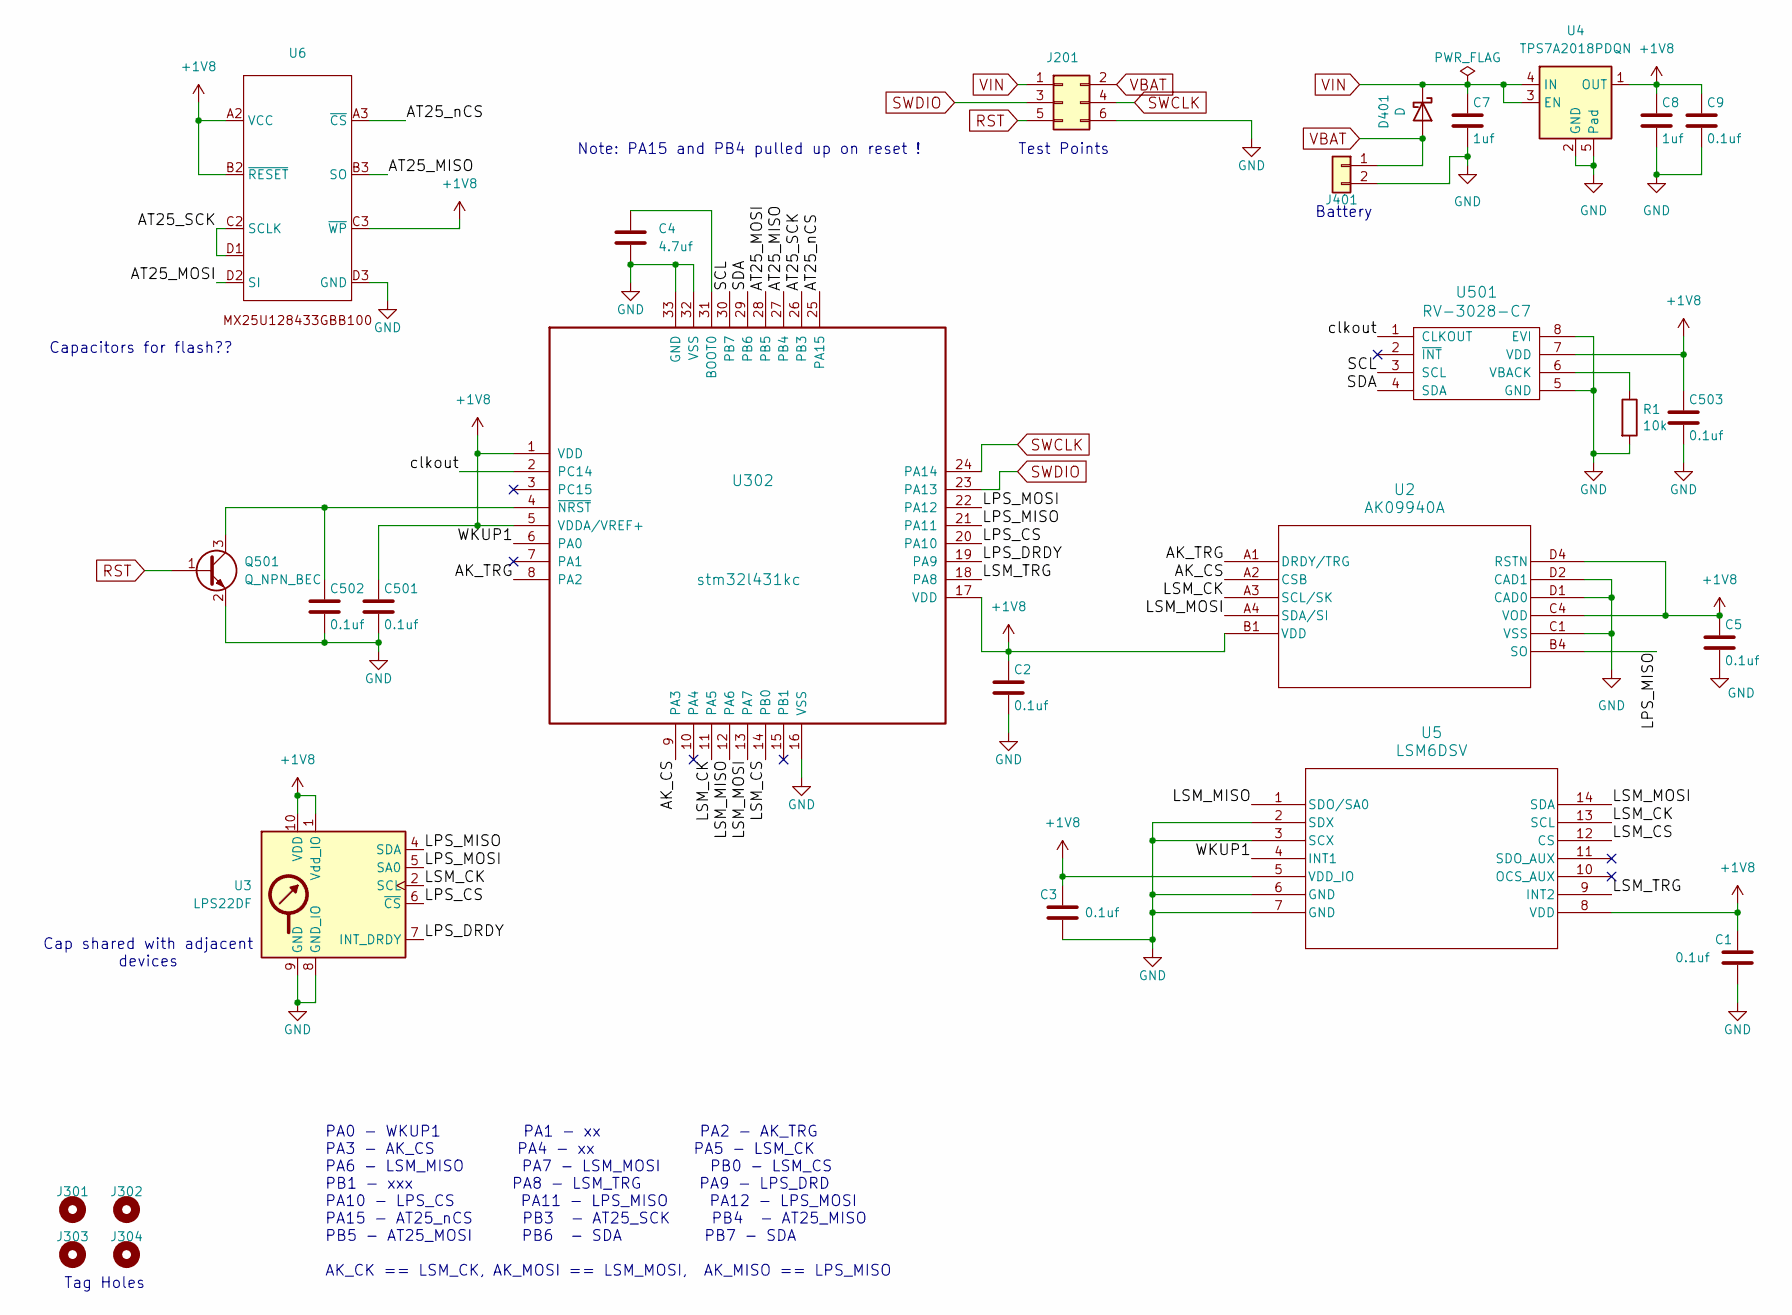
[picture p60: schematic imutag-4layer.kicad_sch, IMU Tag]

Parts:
C1, C2, C3, C5, C9, C501, C502, C503: 0.1uf; C_0201_0603Metric; MPN GRM033C81E104KE14D; LCSC C181047
C4: 4.7uf; C_0201_0603Metric; MPN GRM035R60J475ME15D; LCSC C335103
C7, C8: 1uf; C_0201_0603Metric; MPN GRM033R60J105MEA2D; LCSC C76930
D401: D; D_0402_1005Metric; MPN CDBQC0130L-HF; LCSC C2886012
J201: CONN_02X04; tagpoints6
J301, J302, J303, J304: Conn_01x01; taghole1.1mm
J401: CONN_01X02; batterypads
Q501: Q_NPN_BEC; SOT-883; MPN BC847AMB,315; LCSC C686658
R1: 10k; R_0201_0603Metric; MPN RC0201FR-0710KL; LCSC C106225
U2: AK09940A; AK09940a; MPN AK09940A
U3: LPS22DF; ST_HLGA-10_2x2mm_P0.5mm_LayoutBorder3x2y
U4: TPS7A2018PDQN; Texas_X2SON-4_1x1mm_P0.65mm; MPN TPS7A2018PDQNR
U5: LSM6DSV; LGA14-L_2P59X3P1X0P5_STM
U6: IC_MX25U12843GBBI00; MPN MX25U12843GBBI00; LCSC C7316586
U302: stm32l431kc; QFN-32-1EP_5x5mm_P0.5mm_EP3.45x3.45mm; MPN STM32L432KCU6; LCSC C1337280
U501: RV-3028-C7; RV-8803-C7; MPN RV-3028-C7 32.768KHZ 1PPM-TA-QA; LCSC C3019759

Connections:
+1V8: C1.1, C2.1, C3.1, C5.1, C8.1, C9.1, C501.1, C503.1, U2.B1 (VDD), U2.C4 (VOD), U2.D4 (RSTN), U3.1 (Vdd_IO), U3.10 (VDD), U4.1 (OUT), U5.5 (VDD_IO), U5.8 (VDD), U6.A2 (VCC), U6.B2 (~RESET), U6.C3 (~WP), U302.1 (VDD), U302.5 (VDDA/VREF+), U302.17 (VDD), U501.7 (VDD)
/AK_CS: U2.A2 (CSB), U302.9 (PA3)
/AK_TRG: U2.A1 (DRDY/TRG), U302.8 (PA2)
/AT25_MISO: U6.B3 (SO), U302.27 (PB4)
/AT25_MOSI: U6.D2 (SI), U302.28 (PB5)
/AT25_SCK: U6.C2 (SCLK), U6.D1, U302.26 (PB3)
/AT25_nCS: U6.A3 (~CS), U302.25 (PA15)
/LPS_CS: U3.6 (~CS), U302.20 (PA10)
/LPS_DRDY: U3.7 (INT_DRDY), U302.19 (PA9)
/LPS_MISO: U2.B4 (SO), U3.4 (SDA), U302.21 (PA11)
/LPS_MOSI: U3.5 (SA0), U302.22 (PA12)
/LSM_CK: U2.A3 (SCL/SK), U3.2 (SCL), U5.13 (SCL), U302.11 (PA5)
/LSM_CS: U5.12 (CS), U302.14 (PB0)
/LSM_MISO: U5.1 (SDO/SA0), U302.12 (PA6)
/LSM_MOSI: U2.A4 (SDA/SI), U5.14 (SDA), U302.13 (PA7)
/LSM_TRG: U5.9 (INT2), U302.18 (PA8)
/SCL: U302.30 (PB7), U501.3 (SCL)
/SDA: U302.29 (PB6), U501.4 (SDA)
/WKUP1: U5.4 (INT1), U302.6 (PA0)
/clkout: U302.2 (PC14), U501.1 (CLKOUT)
GND: C1.2, C2.2, C3.2, C4.1, C5.2, C7.2, C8.2, C9.2, C501.2, C502.2, C503.2, J201.6, J401.2, Q501.2 (E), R1.2, U2.C1 (VSS), U2.D1 (CAD0), U2.D2 (CAD1), U3.3 (GND), U3.8 (GND_IO), U3.9 (GND), U4.2 (GND), U4.5 (Pad), U5.2 (SDX), U5.3 (SCX), U5.6 (GND), U5.7 (GND), U6.D3 (GND), U302.16 (VSS), U302.32 (VSS), U302.33 (GND), U501.5 (GND), U501.8 (EVI)
unnamed: C502.1, Q501.3 (C), U302.4 (~NRST)
unnamed: C4.2, U302.31 (BOOT0)
unnamed: R1.1, U501.6 (VBACK)
RST: J201.5, Q501.1 (B)
SWCLK: J201.4, U302.24 (PA14)
SWDIO: J201.3, U302.23 (PA13)
VBAT: D401.2 (A), J201.2, J401.1
VIN: C7.1, D401.1 (K), J201.1, U4.3 (EN), U4.4 (IN)

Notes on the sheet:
Note: PA15 and PB4 pulled up on reset !
Capacitors for flash??
Tag Holes
Test Points
PA0 - WKUP1 PA1 - xx PA2 - AK_TRG PA3 - AK_CS PA4 - xx PA5 - LSM_CK PA6 - LSM_MISO PA7 - LSM_MOSI PB0 - LSM_CS PB1 - xxx PA8 - LSM_TRG PA9 - LPS_DRD PA10 - LPS_CS PA11 - LPS_MISO PA12 - LPS_MOSI PA15 - AT25_nCS PB3 - AT25_SCK PB4 - AT25_MISO PB5 - AT25_MOSI PB6 - SDA PB7 - SDA AK_CK == LSM_CK, AK_M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
Battery
Cap shared with adjacent devices

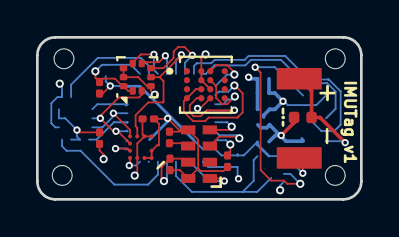
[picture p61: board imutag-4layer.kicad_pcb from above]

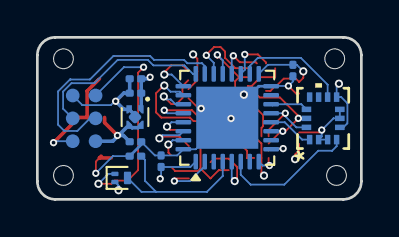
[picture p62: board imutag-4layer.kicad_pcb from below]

Board: 4 copper layers, 18.0 x 9.0 mm, 27 parts (11 on the bottom side), 29 nets.

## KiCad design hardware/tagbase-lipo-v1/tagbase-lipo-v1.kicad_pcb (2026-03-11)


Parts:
C1, C4, C5, C104: 1uF; C_0402_1005Metric; MPN CL05A105KA5NQNC; LCSC C52923
C2, C101, C107: 0.1uF; C_0402_1005Metric; MPN CL05B104KO5NNNC; LCSC C1525
C6, C7: 4.7uf; C_0402_1005Metric; MPN CL05A475MP5NRNC; LCSC C23733
D1: D_Schottky_Small; D_SOD-323; MPN 1N5819WS; LCSC C191023
D101: LED-RED; D_0805_2012Metric; MPN NCD0805R1; LCSC C84256
D102, D105: LED-GREEN; D_0805_2012Metric; MPN KT-0805G; LCSC C2297
H1, H2, H3, H4: MountingHole; MountingHole_2.5mm; not fitted
J1: Conn_01x04_Female; JST_XH_B04B-XH-AM_1x04_P2.50mm_Vertical; not fitted
J2: Conn_01x06; JST_B6B-ZR(LF)(SN); not fitted
J5: Conn_01x02; PinHeader_1x02_P2.54mm_Vertical; not fitted
J101: Conn_02x03_Odd_Even; 6pin_tagpoints_double_screws; not fitted
J102: Conn_02x05_Odd_Even; FTSH-105-01-F-D-K; not fitted
J104: USB_B_Mini; USB_Mini-B; MPN MINI 5PTP; LCSC C2681563
R1: 33K; R_0402_1005Metric; MPN 0402WGF3302TCE; LCSC C25779
R2, R3: 10K; R_0402_1005Metric; MPN 0402WGF1002TCE; LCSC C25744
R4: 1K; R_0402_1005Metric; MPN 0402WGF1001TCE; LCSC C11702
R5, R102: 100; R_0603_1608Metric; MPN 0603WAF1000T5E; LCSC C22775
R101: 220; R_0603_1608Metric; MPN 0603WAF1000T5E; LCSC C22775
R104: 2.2K; R_0402_1005Metric; MPN 0402WGF2201TCE; LCSC C25879
SW1, SW2: SW_SPDT; CJS-1200B_NDC; MPN CJS-1201B; LCSC C132858
U1: XC6206P332MR; SOT-23-3; MPN XC6206P332MR; LCSC C5446
U2: XC6808ANC28R-G; USP-6B_TOR; MPN XC6808A4C28R-G; LCSC C3682502
U3: XC6206P202MR; SOT-23-3; MPN XC6206P202MR-G; LCSC C2891260
U4: STM32C071GBU6N; UFQFPN-28_STM; MPN STM32C071GBU6N; LCSC C42240018
U105: Tactile Switch; SW_SPST_TS_1187; MPN TS-1187A-C-E-B; LCSC C318889

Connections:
+2V: C2.1, C5.1, C6.1, R3.1, U3.2 (VO), U4.3 (VDD/VDDA)
+3V3: C7.1, C104.1, C107.1, D101.2 (A), D102.2 (A), D105.2 (A), J102.1, SW1.3 (C), U1.2 (VO), U4.17 (VDDIO2), U105.2 (B)
/BAT: SW2.1 (A), U2.1 (BAT)
/CSO: R3.2, U2.3 (CSO), U4.11 (PA5), U4.12 (PA6)
/LED_GREEN: R102.2, U4.16 (PA8)
/LED_RED: R101.2, U4.22 (PA15)
/NRST: C101.1, J102.10, U4.5 (PF2-NRST)
/SWCLK: J102.4, U4.21 (PA14-BOOT0), U105.1 (A)
/SWDIO: J102.2, U4.20 (PA13)
/UART_TX: J5.2, U4.26 (PB6)
/USB_DM: J104.2 (D-), U4.18 (PA11[PA9])
/USB_DP: J104.3 (D+), U4.19 (PA12[PA10])
GND: C1.2, C2.2, C4.2, C5.2, C6.2, C7.2, C101.2, C104.2, C107.2, J1.4, J2.1, J5.1, J101.2, J102.3, J102.5, J102.9, J104.4 (ID), J104.5 (GND), J104.6 (Shield), R1.2, R2.2, R5.2, U1.1 (GND), U2.2 (VSS), U2.7 (EPAD), U3.1 (GND), U4.4 (VSS/VSSA)
unnamed: D1.2 (A), SW1.2 (B)
unnamed: D101.1 (K), R101.1
unnamed: D102.1 (K), R102.1
unnamed: D105.1 (K), R5.1
unnamed: R1.1, U2.4 (ISET)
unnamed: R2.1, U2.5 (THIN/NF)
unnamed: R4.1, U4.8 (PA2)
unnamed: R104.2, U4.27 (PB7)
TAG_3V3: D1.1 (K), J2.6, J101.5
TAG_3V3_IN: J1.2, SW1.1 (A)
TAG_RESET: J2.3, J101.1, R104.1
TAG_SCK: J2.4, J101.4, U4.6 (PA0), U4.7 (PA1)
TAG_SWDIO: J2.2, J101.3, R4.2, U4.10 (PA4)
TAG_VBAT: J2.5, J101.6, SW2.2 (B)
VUSB: C1.1, C4.1, J104.1 (VBUS), U1.3 (VI), U2.6 (VIN), U3.3 (VI)

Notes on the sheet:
Rset = 351K * Icharge(mA)^-1.1 e.g Rset(10mA) = 351/(12.6) = 27.9K Rset(9.35mA) = 30K Rset(8.58mA) = 33K
No need for pulldown on PA14 -- weak internal pull-down activated on reset
DFU - pullup, weak pulldown on pin
Red 2Vf, 6mA, 216 ohm (3.3v) Green 2.7Vf, 6mA, 100 ohm (3.3V) Green 2.7Vf, 6mA, 300 ohm (4.5V)

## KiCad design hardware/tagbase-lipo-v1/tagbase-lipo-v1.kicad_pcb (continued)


Board: 2 copper layers, 50.8 x 69.9 mm, 38 parts (0 on the bottom side), 28 nets.

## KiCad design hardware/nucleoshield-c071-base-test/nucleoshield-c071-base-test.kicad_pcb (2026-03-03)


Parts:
J1: Power; PinSocket_1x08_P2.54mm_Vertical
J2: Digital/PWM; PinSocket_1x10_P2.54mm_Vertical
J3: Analog; PinSocket_1x06_P2.54mm_Vertical
J4: Digital/PWM; PinSocket_1x08_P2.54mm_Vertical
J5: Conn_02x03_Odd_Even; 6pin_tagpoints_new_offset
NT1, NT3, NT4, NT5, NT6, NT7: NetTie_2; NetTie-2_SMD_Pad0.5mm
NT2: NetTie_3; NetTie-3_SMD_Pad0.5mm
R1: 1K; R_1206_3216Metric_Pad1.30x1.75mm_HandSolder

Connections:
+3V3: J1.4, NT7.1
/AREF: J2.3
/IOREF: J1.2
/PA0: J3.1, NT2.1
/PA1: J3.2, NT2.3
/PA4: J3.3, NT6.1
/PA5: J2.5
/PA6: J2.6
/PA7: J2.7, NT3.1
/PA8: J4.1
/PA9: J2.10
/PA10: J4.6, NT4.1
/PA15: J2.8
/PB0: J3.4
/PB3: J2.9
/PB4: J4.3
/PB5: J4.4
/PB8: J2.1
/PB9: J2.2
/PC4: J3.5
/PC5: J3.6
/PC7: J4.5
/PC8: J4.2
/RX/PB7: J4.8
/SPI1_MOSI: NT3.2, R1.2
/SPI2_MOSI: NT1.1, NT4.2
/TX/PB6: J4.7
/~RESET: J1.3
GND: J1.6, J1.7, J2.4, J5.2
TAG_3V3: J5.5, NT7.2
TAG_RESET: J5.1, NT6.2
TAG_SCK: J5.4, NT2.2
TAG_SWDIO: J5.3, NT1.2, R1.1
TAG_VBAT: J5.6, NT5.2

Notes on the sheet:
PA0 SPI2_SCK PA1 SPI1_SCK PA4 SPI2_MOSI PB0 PC4 PC5
* Indicates a PWM-capable pin
PA8 PC8 PB4 SPI1_MISO PB5 SPI1_MOSI PC7 PA10 SPI2_MOSI PB6 SPI2_MISO PB7 SPI2_MOSI
PB8 SPI2_SCK PB9 PA5 SPI1_SCK PA6 SPI1_MISO PA7 SPI1_MOSI PA15 PB3 SPI1_SCK PA9 SPI2_MISO



Board: 2 copper layers, 50.0 x 53.4 mm, 13 parts (8 on the bottom side), 14 nets.

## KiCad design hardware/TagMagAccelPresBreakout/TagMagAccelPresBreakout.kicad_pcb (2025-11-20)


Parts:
C1: 0.1uf; C_0201_0603Metric; MPN GRM033C81E104KE14D; LCSC C181047
C2, C5, C6, C7, C501, C502, C503: 0.1uf; C_0201_0603Metric; MPN GRM033C81E104KE14D
C4: 47uf; C_0603_1608Metric; MPN 06036D476MAT2A
C8, C9, C101: 1uf; C_0201_0603Metric; MPN GRM033R60J105MEA2D
C404: 22uf; C_0402_1005Metric; MPN 04026D226MAT2A
D401: D; D_0402_1005Metric; MPN CDBQC0130L-HF
H1, H2, H3, H4: MountingHole; MountingHole_2.5mm
J1: Conn_01x06; CONN_B6B-ZR_JST
J2: Conn_01x04; PinHeader_1x05_P2.54mm_Vertical
J3: Conn_01x04; PinHeader_1x04_P2.54mm_Vertical
J4, J5: Conn_01x06; PinHeader_1x06_P2.54mm_Vertical
J6: Conn_02x04_Counter_Clockwise; PinHeader_2x04_P2.54mm_Vertical
J401: CONN_01X02; MS621
Q501: Q_NPN_BEC; SOT-883; MPN BC847AMB,315
R1: 10k; R_0201_0603Metric; MPN RC0201FR-0710KL
U1: at25xe321D-UUN; adesto_wlcsp12; MPN AT25XE321D-UUN-T
U2: LIS2DU12TR; LGA-12L_LIS2DU12_STM; MPN LIS2DU12TR
U3: LPS27HHWTR; MPN LPS27HHTWTR
U4: AK09940A; AK09940a; MPN AK09940A
U5: TPS7A2018PDQN; Texas_X2SON-4_1x1mm_P0.65mm; MPN TPS7A2018PDQNR
U302: stm32l431kc; QFN-32-1EP_5x5mm_P0.5mm_EP3.45x3.45mm; MPN STM32L431KCU6
U501: RV-3028-C7; RV-8803-C7; MPN RV-3028-C7 32.768KHZ 1PPM-TA-QC

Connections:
+1V8: C5.1, C9.1, J6.3, U4.C4 (VOD), U5.1 (OUT)
+2V5: C1.1, C2.1, C4.1, C8.1, C101.1, C404.1, C501.1, C503.1, D401.1 (K), J1.6, U1.B2 (VCC), U1.D2 (~RESET), U2.9 (VDD), U2.10 (VDD_IO), U5.4 (IN), U302.1 (VDD), U302.5 (VDDA/VREF+), U302.17 (VDD), U501.7 (VDD)
/AK_CS: J6.2, U4.A2 (CSB), U302.15 (PB1)
/AK_PWR: C7.1, J6.8, U4.B1 (VDD), U5.3 (EN), U302.22 (PA12)
/AK_RSTN: J6.7, U4.D4 (RSTN), U302.21 (PA11)
/AK_USART1_CK: J6.4, U4.A3 (SCL/SK), U302.18 (PA8)
/AK_USART1_RX: J6.6, U4.B4 (SO), U302.20 (PA10)
/AK_USART1_TX: J6.5, U4.A4 (SDA/SI), U302.19 (PA9)
/AT25_MISO: J2.3, U1.D4 (SO), U302.27 (PB4)
/AT25_MOSI: J2.2, U1.E3 (SI), U302.28 (PB5)
/AT25_SCK: J2.5, U1.F2 (SCK), U302.26 (PB3)
/AT25_nCS: J2.4, U1.B4 (nCS), U302.25 (PA15)
/LIS_CS: J4.4, U2.2 (CS), U302.14 (PB0)
/LIS_INT1: J4.6, U2.12 (INT1), U302.6 (PA0)
/LIS_MISO: J4.3, U2.3 (SDO/SA0), U302.12 (PA6)
/LIS_MOSI: J4.2, U2.4 (SDA/SDI/SDO), U302.13 (PA7)
/LIS_SCK: J4.5, U2.1 (SCL/SPC), U302.11 (PA5)
/LPS_CS: J5.4, U3.6 (CS), U302.3 (PC15)
/LPS_PWR: C6.1, J5.3, U3.1 (VDD_IO), U3.10 (VDD), U302.7 (PA1)
/LPS_RX: J5.5, U3.5 (SDO/SA0), U302.8 (PA2)
/LPS_SCK: J5.2, U3.2 (SCL/SPC), U302.10 (PA4)
/LPS_TX: J5.6, U3.4 (SDA/SDI/SDO), U302.9 (PA3)
/RST: J1.3, J3.3, Q501.1 (B)
/RTC_SCL: U302.30 (PB7), U501.3 (SCL)
/RTC_SDA: U302.29 (PB6), U501.4 (SDA)
/VBAT: D401.2 (A), J1.5, J401.1
/clkout: U302.2 (PC14), U501.1 (CLKOUT)
GND: C1.2, C2.2, C4.2, C5.2, C6.2, C7.2, C8.2, C9.2, C101.2, C404.2, C501.2, C502.2, C503.2, J1.1, J2.1, J3.1, J4.1, J5.1, J6.1, J401.2, Q501.2 (E), R1.2, U1.C3 (GND), U2.6 (GND), U2.7 (RES), U2.8 (GND), U3.3 (RES), U3.8 (GND), U3.9 (GND), U3.11 (GND), U4.C1 (VSS), U4.D1 (CAD0), U4.D2 (CAD1), U5.2 (GND), U5.5 (Pad), U302.16 (VSS), U302.31 (BOOT0), U302.32 (VSS), U302.33 (GND), U501.5 (GND), U501.8 (EVI)
unnamed: C502.1, Q501.3 (C), U302.4 (~NRST)
unnamed: R1.1, U501.6 (VBACK)
SWCLK: J1.4, J3.2, U302.24 (PA14)
SWDIO: J1.2, J3.4, U302.23 (PA13)

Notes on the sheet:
TX/RX pin swap works for USART -- CR2_SWAP
Battery
SPI3
Note: PA15 and PB4 pulled up on reset !
I2C1
WARNING -- POWER LINES REVERSED on AK09940A
Note LPS_RX/LPS_TX swapped -- must be configured in software
USART2
SPI1
USART1


Board: 2 copper layers, 50.0 x 35.0 mm, 34 parts (0 on the bottom side), 32 nets.

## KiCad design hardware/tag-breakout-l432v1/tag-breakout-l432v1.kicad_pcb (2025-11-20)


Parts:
C1, C104: 1uF; C_0603_1608Metric; MPN CL10A105KB8NNNC; LCSC C15849
C2, C11, C101, C107: 0.1uF; C_0603_1608Metric; MPN CC0603KRX7R9BB104; LCSC C14663
D1: LED-GREEN; LED_0603_1608Metric; MPN P0603P1N46G12; LCSC C5123548
D2, D3: D_Schottky; D_SOD-123; LCSC C8598
D105: LED-RED; LED_0603_1608Metric; MPN KT 0603R; LCSC C2286
J1: Conn_01x04_Female; JST_XH_B04B-XH-AM_1x04_P2.50mm_Vertical; not fitted
J2: Conn_01x02_Male; PinHeader_1x02_P2.54mm_Vertical; not fitted
J102: Conn_02x05_Odd_Even; FTSH-105-01-F-D-K; not fitted
J104: USB_B_Mini; USB_Mini-B_Lumberg_2486_01_Horizontal; MPN MINI 5PTP; LCSC C2681563
R1, R107: 620; R_0603_1608Metric; MPN 0603WAF6200T5E; LCSC C23220
R2: 35.7; R_0603_1608Metric; LCSC C158925
R4, R104: 2.2K; R_0603_1608Metric; MPN 0603WAF1002T5E; LCSC C4190
R5: 82; R_0603_1608Metric; LCSC C23255
R6: 100; R_0603_1608Metric; MPN 0603WAF1000T5E; LCSC C22775
R105: 10K; R_0603_1608Metric; MPN 0603WAF1002T5E; LCSC C25804
R106: 200; R_0603_1608Metric; MPN 0603WAF1000T5E; LCSC C8218
SW1: SW_DIP_x04; SW_DIP_SPSTx04_Slide_KingTek_DSHP04TS_W7.62mm_P1.27mm; MPN DSHP04TSGET; LCSC C40736
TP1: SWDIO; TestPoint_Pad_D2.0mm
TP2: SCK; TestPoint_Pad_D2.0mm
U1: XC6206; SOT-23-3; MPN XC6206P332MR; LCSC C5446
U4: TS5A3159ADBVR; SOT-23-6; MPN TS5A3159ADBVR; LCSC C128405
U101: STM32F042K6Tx; LQFP-32_7x7mm_P0.8mm; LCSC C69216
U105: Tactile Switch; SW_SPST_TS_1187; MPN TS-1187A-C-E-B; LCSC C318889

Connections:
+3V3: C2.1, C11.1, C104.1, C107.1, J102.1, U1.2 (VO), U4.3, U4.5 (V+), U101.1 (VDD), U101.5 (VDDA), U101.17 (VDDIO2), U105.2 (B)
/LED_GREEN: D1.2 (A), U101.26 (PB3)
/NRST: C101.1, J102.10, U101.4 (NRST)
/SCLK: J102.4, U101.24 (PA14)
/SWDIO: J102.2, U101.23 (PA13)
/UART_TX: J2.1, U101.29 (PB6)
/USB_DM: J104.2 (D-), U101.21 (PA11)
/USB_DP: J104.3 (D+), U101.22 (PA12)
/boot0: R105.2, U101.31 (PB8), U105.1 (A)
EXT_PWR: D3.2 (A), J1.3, R4.1, U4.6
GND: C1.2, C2.2, C11.2, C101.2, C104.2, C107.2, J1.4, J2.2, J102.3, J102.5, J102.9, J104.4 (ID), J104.5 (GND), J104.6 (Shield), R1.2, R4.2, R105.1, R107.2, U1.1 (GND), U4.2 (GND), U101.16 (VSS), U101.32 (VSSA); also elsewhere on the board
unnamed: D1.1 (K), R1.1
unnamed: C1.1, D2.1 (K), D3.1 (K), U1.3 (VI)
unnamed: D105.1 (K), R107.1
unnamed: R2.1, SW1.2
unnamed: R2.2, R5.2, R6.2, SW1.1, U4.4
unnamed: R5.1, SW1.3
unnamed: R6.1, SW1.4
unnamed: R104.2, U101.6 (PA0)
unnamed: R106.1, U101.13 (PA7)
PWR_IN: J1.2, U4.1
PWR_IN_MIRROR: J1.1, U101.15 (PB1)
TAG_3V3: SW1.5, SW1.6, SW1.7, SW1.8; also elsewhere on the board
TAG_RESET: R104.1; also elsewhere on the board
TAG_SCK: TP2.1, U101.11 (PA5); also elsewhere on the board
TAG_SWDIO: R106.2, TP1.1, U101.12 (PA6); also elsewhere on the board
VUSB: D2.2 (A), D105.2 (A), J104.1 (VBUS)


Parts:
C3, C4, C5, C6, C7, C9: 0.1uF; C_0603_1608Metric; MPN CC0603KRX7R9BB104; LCSC C14663
C10: 4.7uF; C_0603_1608Metric; LCSC C19666
J3, J4: Conn_01x17; PinHeader_1x17_P2.54mm_Vertical_Staggered; not fitted
Q1: Q_NPN_BEC; SOT-23; LCSC C20527
R3: 10K; R_0603_1608Metric; MPN 0603WAF1002T5E; LCSC C25804
U3: stm32l432; UFQFPN-32-1EP_5x5mm_P0.5mm_EP3.5x3.5mm; LCSC C94784
U6: RV-3028-C7; RV-8803-C7; LCSC C3019759

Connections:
/stm32/NRST: C5.1, Q1.3 (C), U3.4 (~NRST)
/stm32/PA0: J3.8, U3.6 (PA0)
/stm32/PA1: J3.9, U3.7 (PA1)
/stm32/PA2: J3.10, U3.8 (PA2)
/stm32/PA3: J3.11, U3.9 (PA3)
/stm32/PA4: J3.12, U3.10 (PA4)
/stm32/PA5: J3.13, U3.11 (PA5)
/stm32/PA6: J3.14, U3.12 (PA6)
/stm32/PA7: J3.15, U3.13 (PA7)
/stm32/PA8: J4.8, U3.18 (PA8)
/stm32/PA9: J4.7, U3.19 (PA9)
/stm32/PA10: J4.6, U3.20 (PA10)
/stm32/PA11: J4.5, U3.21 (PA11)
/stm32/PA12: J4.4, U3.22 (PA12)
/stm32/PA15: J4.3, U3.25 (PA15)
/stm32/PB0: J3.16, U3.14 (PB0)
/stm32/PB1: J4.16, U3.15 (PB1)
/stm32/PB2: J4.15
/stm32/PB3: J4.2, U3.26 (PB3)
/stm32/PB4: J3.1, U3.27 (PB4)
/stm32/PB5: J3.2, U3.28 (PB5)
/stm32/PB8: J3.5
/stm32/PB9: J3.6
/stm32/PB10: J4.14
/stm32/PB11: J4.13
/stm32/PB12: J4.12
/stm32/PB13: J4.11
/stm32/PB14: J4.10
/stm32/PB15: J4.9
/stm32/VBACK: R3.2, U6.6 (VBACK)
/stm32/clkout: U3.2 (PC14), U6.1 (CLKOUT)
/stm32/rtc_scl: J3.3, U3.29 (PB6), U6.3 (SCL)
/stm32/rtc_sda: J3.4, U3.30 (PB7), U6.4 (SDA)
GND: C3.2, C4.2, C5.2, C6.2, C7.2, C9.2, C10.2, J3.17, J4.17, Q1.2 (E), R3.1, U3.16 (VSS), U3.31 (BOOT0), U3.32 (VSS), U3.33 (GND), U6.5 (GND), U6.8 (EVI); also elsewhere on the board
TAG_3V3: C3.1, C4.1, C6.1, C7.1, C9.1, C10.1, J3.7, J4.1, U3.1 (VDD), U3.5 (VDDA/VREF+), U3.17 (VDD), U6.7 (VDD); also elsewhere on the board
TAG_RESET: Q1.1 (B); also elsewhere on the board
TAG_SCK: U3.24 (PA14); also elsewhere on the board
TAG_SWDIO: U3.23 (PA13); also elsewhere on the board



Board: 2 copper layers, 53.3 x 73.7 mm, 43 parts (2 on the bottom side), 51 nets.

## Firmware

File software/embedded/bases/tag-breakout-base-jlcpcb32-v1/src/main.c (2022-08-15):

/**************************************************************************
*      Copyright 2018  Geoffrey Brown                                     *
*                                                                         *
*                                                                         *
*                                                                         *
* Licensed under the Apache License, Version 2.0 (the "License");         *
* you may not use this file except in compliance with the License.        *
* You may obtain a copy of the License at                                 *
*                                                                         *
*     http://www.apache.org/licenses/LICENSE-2.0                          *
*                                                                         *
* Unless required by applicable law or agreed to in writing, software     *
* distributed under the License is distributed on an "AS IS" BASIS,       *
* WITHOUT WARRANTIES OR CONDITIONS OF ANY KIND, either express or implied.*
* See the License for the specific language governing permissions and     *
* limitations under the License.                                          *
**************************************************************************/

#include "hal.h"
#include "stm32f0xx_ll_crs.h"
#include "usbcfg.h"
#include "app.h"

#define RCC_APB1ENR_CRSN ((uint32_t)0x08000000U)

#define ADC_SMPR_SMP_1P5 0U   /**< @brief 14 cycles conversion time   */
#define ADC_SMPR_SMP_7P5 1U   /**< @brief 21 cycles conversion time.  */
#define ADC_SMPR_SMP_13P5 2U  /**< @brief 28 cycles conversion time.  */
#define ADC_SMPR_SMP_28P5 3U  /**< @brief 41 cycles conversion time.  */
#define ADC_SMPR_SMP_41P5 4U  /**< @brief 54 cycles conversion time.  */
#define ADC_SMPR_SMP_55P5 5U  /**< @brief 68 cycles conversion time.  */
#define ADC_SMPR_SMP_71P5 6U  /**< @brief 84 cycles conversion time.  */
#define ADC_SMPR_SMP_239P5 7U /**< @brief 252 cycles conversion time. */

#define ADC_PA6_CHAN 6
#define ADC_PB1_CHAN 9
#define ADC_VREF_CHAN 17

const uint16_t *ADC_VREF_CAL = ((uint16_t *)0x1FFFF7BA);

volatile uint32_t vlipo100;
static uint32_t vref100;

// Charger LED thread

static THD_WORKING_AREA(waThread1, 512);
static THD_FUNCTION(Thread1, arg)
{

  (void)arg;

  //  chRegSetThreadName("charger");
  while (true)
  {
    chThdSleepMilliseconds(100);

    // don't read ADC if external power connected
#if 0
    if (!palReadLine(LINE_EXT_PWR))
    {
      //palClearLine(LINE_TAG_3V3_EN);
      vlipo100 = 330; // just so that stlink can connect
      continue;
    }
    else
    {
      //palSetLine(LINE_TAG_3V3_EN);
    }
#endif

    adc1Start();
    adc1EnableVREF();
    adc1StartConversion(ADC_VREF_CHAN, ADC_SMPR_SMP_239P5);
    while (adc1Eoc() == false)
      chThdYield();
    adc1DisableVREF();
    vref100 = ((*ADC_VREF_CAL) * 330) / adc1DR();

    // Sample vlipo100
    // enable ADC input

    chThdSleepMilliseconds(10);

    // perform conversion

    //    adc1StartConversion(ADC_PB1_CHAN,ADC_SMPR_SMP_239P5);
    adc1StartConversion(ADC_PA6_CHAN, ADC_SMPR_SMP_239P5);
    while (adc1Eoc() == false)
      chThdYield();

    vlipo100 = (vref100 * adc1DR()) / 4096;
    if (vlipo100 < 200)
      vlipo100 = 330;
  }
}

uint8_t bulkbuf[64]; // stlink input buffer

int main(void)
{

  halInit();

  // Remap the USB pins PA11,PA12 onto the default PA9,PA10

  SYSCFG->CFGR1 |= SYSCFG_CFGR1_PA11_PA12_RMP;

  // Initialize clock recovery system

  rccEnableAPB1(RCC_APB1ENR_CRSEN, 0);
  rccResetAPB1(RCC_APB1RSTR_CRSRST);

  LL_CRS_SetSyncDivider(LL_CRS_SYNC_DIV_1);
  LL_CRS_SetSyncPolarity(LL_CRS_SYNC_POLARITY_RISING);
  LL_CRS_SetSyncSignalSource(LL_CRS_SYNC_SOURCE_USB);
  LL_CRS_SetReloadCounter(__LL_CRS_CALC_CALCULATE_RELOADVALUE(48000000,
                                                              1000));
  LL_CRS_SetFreqErrorLimit(34);
  LL_CRS_SetHSI48SmoothTrimming(32);

  LL_CRS_EnableAutoTrimming();
  LL_CRS_EnableFreqErrorCounter();

  // disable swd line

  palSetLine(LINE_TGT_SWDIO_EN); // polarity is reversed
  palClearLine(LINE_TGT_RESET);

  // Initialize system

  chSysInit();

  // Activate USB driver

  usbDisconnectBus(&USBD1);
  chThdSleepMilliseconds(1500);
  usbStart(&USBD1, &usbcfg);
  usbConnectBus(&USBD1);

  // Create the charger thread

  chThdCreateStatic(waThread1, sizeof(waThread1),
                    NORMALPRIO, Thread1, NULL);

  // process stlink commands

  while (true)
  {
    int n = 0;
    n = BULK_Receive(bulkbuf, 64);
    if (n != 16)
    {
      EPRINTF("received %d bytes expected 16\r\n", n);
      chThdSleepMilliseconds(10);
    }
    else
    {
      palSetLine(LINE_TGT_SWDIO_EN);
      stlink_eval(bulkbuf);
      palClearLine(LINE_TGT_SWDIO_EN);
    }
  }
}

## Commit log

2022-11-25 update PresTag components
    [PresTag-v3.kicad_sch]
2022-12-14 update prestag for manufacturing
    [PresTag-v3-B_Cu.gbl, PresTag-v3-B_Mask.gbs, PresTag-v3-B_Paste.gbp, PresTag-v3-B_Silkscreen.gbo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]
2022-12-21 update Prestag
    [PresTag-v3.kicad_pcb, PresTag-v3.kicad_sch]
2023-02-02 update tagbase
    [tagbase-jlcpcb-v3.kicad_pcb, tagbase-jlcpcb-v3.kicad_sch]
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2023-03-16 revise prestag
    [PresTag-v3.kicad_pcb, PresTag-v3.kicad_sch]
2023-03-17 update prestag hardware
    [PresTag-v3-B_Cu.gbl, PresTag-v3-B_Mask.gbs, PresTag-v3-B_Paste.gbp, PresTag-v3-B_Silkscreen.gbo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]
2023-03-17 checkpoint Prestagv4
    [PresTag-v3.kicad_pcb]
2023-03-17 move prestag pcb origin
    [BitTagvc.scad, PresTag-v3.kicad_pcb]
2023-03-17 update lps27 part number
    [PresTag-v3.kicad_pcb, PresTag-v3.kicad_sch]
2023-03-17 move origin for BitTagv7
    [BitTagv7.kicad_pcb]
2023-03-18 update kibot yaml for prestag
    [PresTag-v3-Edge_Cuts.dxf, PresTag-v3.kicad_pcb]
2023-03-19 developing mechanical for PresTag
    [PresTagv1.scad, test.dxf, test.scad]
2023-04-15 update BitTagvc plastic
    [BitTagvc.scad, BitTagvc.stl]
2023-04-30 Board for spray coating tags
    [panel.kicad_pcb, pcb_coating_tool_array-B_Cu.gbr, pcb_coating_tool_array-B_Mask.gbr, pcb_coating_tool_array-B_Paste.gbr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]
2023-05-03 fix adc
    [pcb_coating_tool_array.kicad_pcb]
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2023-05-13 added PresTagv5
    [CDBQR.step, DSBGA-4.step, Diodes_DFN1006-3.step, LGA-12_2X2X0P93_STM.step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]
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2023-05-19 added BitTagNG pcb
    [BitTagNG.kicad_pcb, BitTagNG.kicad_sch, BitTagNG.sch]
2023-05-27 update tag base plastic
    [BitTagvc.scad, PresTagv1.scad]
2023-05-31 add tagbase v7 for jlcpcb
    [B6B-ZR.STEP, tagbase-jlcpcb-v3.kicad_pcb, tagbase-jlcpcb-v3.kicad_sch]
2023-06-02 added tagbase v7
    [B6B-ZR.STEP, tagbase-jlcpcb-v3.kicad_pcb, tagbase-jlcpcb-v3.kicad_sch]
2023-06-02 update tagbase v7
    [B6B-ZR.STEP, tagbase-jlcpcb-v3.kicad_pcb, tagbase-jlcpcb-v3.kicad_sch]
2023-06-02 renamed tagbase-v7
    [B6B-ZR.STEP, tagbase-v7.kicad_pcb, tagbase-v7.kicad_sch]
2023-06-03 fix tagbase v7 for jlcpcb fabrication
    [tagbase-v7.kicad_pcb, tagbase-v7.kicad_sch]
2023-06-03 added jlcpcb multicharger
    [MultiCharger-Edge_Cuts.dxf, Multicharger-jlcpcb.kicad_pcb, Multicharger-jlcpcb.kicad_sch]
2023-06-04 complete JLCPCB multicharger
    [Multicharger-jlcpcb.kicad_pcb, Multicharger-jlcpcb.kicad_sch]
2023-06-05 archive 3d models
    [Multicharger-jlcpcb.kicad_pcb, tagbase-v7.kicad_pcb]
2023-06-06 convert multicharger for jlcpcb
    [Multicharger-jlcpcb.kicad_pcb, Multicharger-jlcpcb.kicad_sch]
2023-06-11 update clearances for bittag base
    [BitTagvc.scad, multicharger-acrylic.dxf]
2023-06-13 update multicharger
    [Multicharger-jlcpcb.kicad_pcb]
2023-06-26 remove voltage shutdown from BitTag
    [Multicharger-jlcpcb.kicad_sch]
2023-07-08 correct multicharger load resistor part numbers
    [Multicharger-jlcpcb.kicad_sch]
2023-07-08 update multicharger to use basic parts
    [Multicharger-jlcpcb.kicad_sch]
2023-07-09 added comments to multicharger
    [Multicharger-jlcpcb.kicad_sch]
2023-07-09 updated jlcpcb multicharger
    [Multicharger-jlcpcb.kicad_pcb, Multicharger-jlcpcb.kicad_sch]
2023-07-10 added 3d models to BitTagNG
    [BitTagNG.kicad_pcb]
2023-07-12 update multicharger resistors
    [Multicharger-jlcpcb.kicad_pcb, Multicharger-jlcpcb.kicad_sch, bom.csv, designators.csv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]
2023-07-13 reduce pcb board clearance on vc plastic
    [BitTagvc.scad]
2023-07-13 update parts in BitTagNG
    [BitTagNG.kicad_pcb, BitTagNG.kicad_sch, bom.csv, designators.csv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]
2023-07-16 update decoupling for adxl367
    [BitTagNG.kicad_pcb, BitTagNG.kicad_sch]
2023-07-16 update bittagng
    [BitTagNG.kicad_pcb, BitTagNG.kicad_sch]
2023-07-21 optimize BitTagNG pcb
    [BitTagNG.kicad_pcb]
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2023-09-22 update BitTagNG for pcbway
    [BitTagNG.sch]
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2024-03-11 reduced via/track sizes for BitTagNG
    [BitTagNG.kicad_pcb]
2024-03-14 acceltagng proto software
    [designators.csv, positions.csv]
2024-03-27 added capacitor to BitTagNG
    [BitTagNG.kicad_pcb, BitTagNG.kicad_sch]
2024-03-28 reduce pad width of adxl367 to 0.32mm from 0.33mm for pcbway
    [BitTagNG.kicad_pcb]
2024-04-15 started new breakout board
    [FTSH-105-01-F-D-K.stp, RV3028.step, stm32.kicad_sch, stm32.sch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]
2024-04-23 revert BitTagNG footprint for adxl367
    [BitTagNG.kicad_pcb]
2024-05-03 Start BitTagv8
    [BitTagv8.kicad_pcb, BitTagv8.kicad_sch, BitTagv8.sch]
2025-01-13 changed delays for PresTag data
    [BaseConnetorPower.kicad_pcb, BaseConnetorPower.kicad_sch, MultiCharger-Edge_Cuts.dxf, bom.csv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]
2025-01-30 update prestag hardware and software
    [CDBQR.step, DSBGA-4.step, Diodes_DFN1006-3.step, LGA-12_2X2X0P93_STM.step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]
2025-02-05 added bmp581 breakout code and board
    [CDBQR.step, DSBGA-4.step, Diodes_DFN1006-3.step, LGA-12_2X2X0P93_STM.step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]
2025-02-19 tweak design
    [BitTagNG-LIS2DU12.kicad_pcb, LGA-12L_LIS2DU12_STM.step]
2025-02-19 update design
    [BitTagNG-LIS2DU12.kicad_pcb, BitTagNG-LIS2DU12.kicad_pcb-back.kicad_pcb, BitTagNG-LIS2DU12.kicad_sch]
2025-02-28 Pruned inactive software/hardware. See branch archive2-28-25 for pruned files
    [BitTagv5.kicad_pcb, BitTagv5.kicad_sch, panel.kicad_pcb, pcb_coating_tool_array-B_Cu.gbr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]
2025-02-28 updated latest board design
    [BitTagNG-LIS2DU12.kicad_pcb, BitTagNG-LIS2DU12.kicad_sch]
2025-03-13 fixed small issues with qtprogram
    [BitTagvc-base.stl, BitTagvc-lid.stl, BitTagvc.scad]
2025-03-16 adding prestag format
    [steval-daughter-v2.kicad_sch]
2025-03-24 working on compass board
    [B6B-ZR.STEP, BitTagNG-LIS2DU12.kicad_pcb, BitTagNG-LIS2DU12.kicad_sch, CDBQR.step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]
2025-03-25 finish breakout board with mag, accel, pres
    [AK09940a.step, TPS7A20.STEP, TagMagAccelPresBreakout.kicad_pcb, TagMagAccelPresBreakout.kicad_sch]
2025-04-16 designed compass tag
    [B6B-ZR.STEP, BitTagNG-LIS2DU12.kicad_pcb, BitTagNG-LIS2DU12.kicad_pcb-back.kicad_pcb, BitTagNG-LIS2DU12.kicad_sch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]
2025-04-23 added bit/pressure tag design
    [BitPresTag.kicad_pcb, BitPresTag.kicad_sch, BitPresTag.sch, BitTagNG-LIS2DU12.kicad_pcb-back.kicad_pcb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]
2025-04-25 checkpoint hardware designs
    [BitPresTag.kicad_pcb, BitPresTag.kicad_sch, BitPresTagBreakout.kicad_pcb, BitPresTagBreakout.kicad_sch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]
2025-06-04 checkpoint -- order compass proto board
    [BitPresTagBreakout.kicad_pcb, BitPresTagBreakout.kicad_sch, CompassTagBreakout.kicad_pcb, CompassTagBreakout.kicad_sch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]
2025-06-05 change drill file location
    [CC-12-4_ADI.step, Multicharger-jlcpcb.csv, PresTag-v3.csv, PresTag-v5.kicad_pcb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]
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2025-06-05 update proto boards
    [BitPresTagBreakout.kicad_sch, CompassTagBreakout.kicad_pcb, stm32.kicad_sch, tag-breakout-l432v1.kicad_pcb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]
2025-06-06 update prototype boards
    [BitPresTagBreakout.kicad_pcb, BitPresTagBreakout.kicad_sch, tag-breakout-l432v1.kicad_pcb, tag-breakout-l432v1.kicad_sch]
2025-06-18 Working board file for tag-breakout-base-l432-v1
    [tag-breakout-l432v1.kicad_pcb, tag-breakout-l432v1.kicad_sch]
2025-09-12 BitTag case design
    [BitTagCase.scad, BitTagCase.stl, BitTagv7-Edge_Cuts.dxf, roundedcube.scad]
2025-09-15 3d model of bittag case
    [BitTagCase-basev2.stl, BitTagCase-lidv2.stl, BitTagCase.scad, BitTagv7.step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]
2025-09-19 compass tag sensor calibration working
    [BitTagCase-basev3.stl, BitTagCase-basev4.stl, BitTagCase-lidv3.stl, BitTagCase-lidv4.stl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]
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2025-11-02 tweak compasstag
    [BitTagCase.scad, CompassTag.kicad_pcb]
2025-12-29 compass tag base
    [CompassTag.FCStd, CompassTagv1.scad]
2026-01-05 tweek compass tag
    [CompassTag.kicad_pcb, CompassTag.kicad_sch, MS920SE-FL27E.STEP]
2026-02-11 add imu tag
    [BitTagNG-LIS2DU12.kicad_pcb-back.kicad_pcb, LGA-12L_LIS2DU12_STM.step, LGA14-L_2P59X3P1X0P5_STM.step, imutag.kicad_pcb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]
2026-02-13 complete IMU tag
    [imutag.kicad_pcb, lipo.scad, lipo.step, lipo.stl]
2026-02-26 update compasstag hardware
    [CompassTag.kicad_pcb, CompassTag.kicad_sch, CompassTagV1.FCStd, CompassTagv1.scad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]
2026-02-26 update parts
    [CompassTag.kicad_pcb, CompassTag.kicad_sch]
2026-03-02 update flash for imu tag
    [CompassTag.kicad_pcb, CompassTag.kicad_sch, imutag.kicad_pcb, imutag.kicad_sch]
2026-03-03 added base test board
    [nucleoshield-c071-base-test.kicad_pcb, nucleoshield-c071-base-test.kicad_sch]
2026-03-03 added nucleoshield template
    [B6B-ZR.STEP, BaseDaughterTemplate.kicad_pcb, BaseDaughterTemplate.kicad_sch, imutag.kicad_pcb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]
2026-03-04 imu breakout board
    [B6B-ZR.STEP, HLGA_10L_STM.step, imutag-daughtercard.kicad_pcb, imutag-daughtercard.kicad_sch]
2026-03-11 restructure data logging
    [tagbase-lipo-v1.kicad_pcb, tagbase-lipo-v1.kicad_sch]
2026-03-15 imu tag breakout
    [RV3028.step, imutag-daughtercard.kicad_sch, imutag.kicad_pcb, imutag.kicad_sch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]
2026-03-27 test of 4 layer imu board
    [BitTagNG-LIS2DU12.kicad_pcb-back.kicad_pcb, LGA-12L_LIS2DU12_STM.step, imutag-4layer.kicad_pcb, imutag-4layer.kicad_sch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]
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

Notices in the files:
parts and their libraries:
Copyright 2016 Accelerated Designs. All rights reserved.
